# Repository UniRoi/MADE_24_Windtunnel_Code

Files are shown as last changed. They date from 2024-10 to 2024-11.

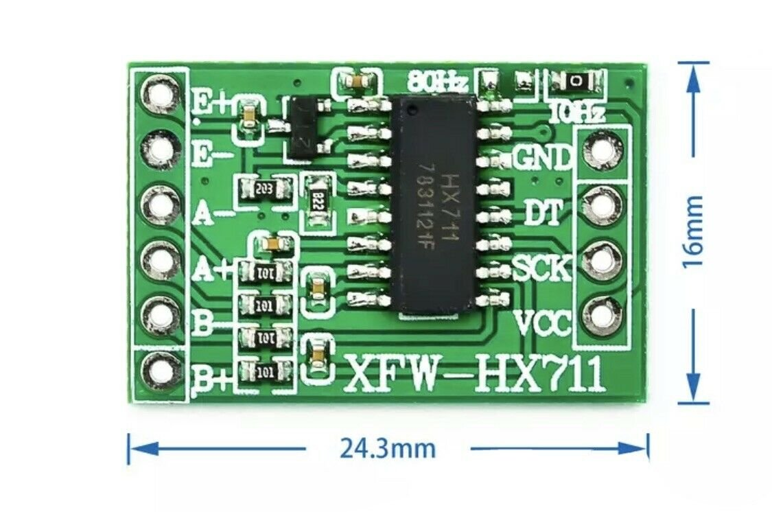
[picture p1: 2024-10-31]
Windtunnel_Schematic/xfw_hx711_picture.png

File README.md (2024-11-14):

# MADE_24_Windtunnel_Code
## Repository for the MADE course at Reykjavik University (RU)
This repository provides resources for the Precision Machine Design course taught in the fall semester of 2024 at Reykjavik University.    
It supports project organization, code structure, and documentation for wind tunnel simulations and data analysis.

## Overview
The MADE_24_Windtunnel_Code repository offers:

### DOCS:
Datasheets, images and project raw data

### Windtunnel_Code:
This folder holds the main code for controlling and operating the wind tunnel system in the `src` and `include` folder.  
Platform IO was used for the development and the library versions are specified in the `platform.ini` file. If this project is compiled for the first time, platform IO will automatically download the necessary libraries and install them on the system.  

The `src_old` folder contains different stages of the project's development:
- `main_calib.cpp`: Initial calibration file from the HX711_ADC library.
- `main_calib_new.cpp`: Modified calibration file from the HX711_ADC library.
- `main_2loadcells.cpp`: First working code for the two-axis load cell
- `main.cpp`: First tests with the LCD.

### Windtunnel_General_Calculations:
Includes general calculation tools, along with pictures and schematics, for analyzing wind tunnel data.  

There are two subfolders in this folder, each requires a virtual pyhton environment to run the jupyter notebook file. Once the environment is created the necessary packages need to be installed with this comand: `pip install -r requirements.txt`
Each folder contains it's own `requirements.txt` file.

#### Evaluating Test Results
Multiple Jupyther notebooks to evaluate the raw data in the `Docs` folder. 

#### Platform Angular Adjustment
Jupyter notebook to calculate the platform angle for different configuration of the linkage.  

### Windtunnel_Schematic:

KICAD 8.0 was used to draw the schematic for the measurement system. This repository also includes a 3D model of the PCB and the libraries for the XFW-HX711 module.

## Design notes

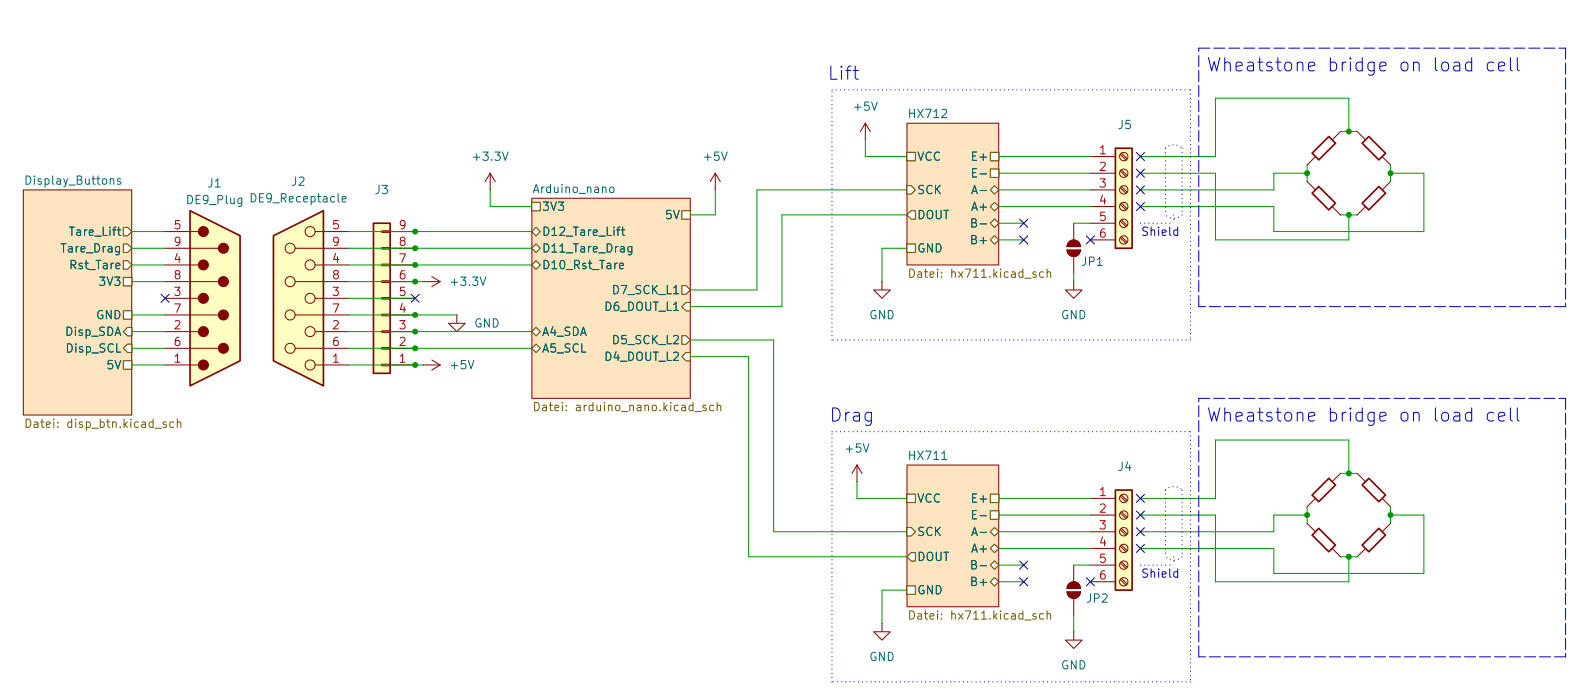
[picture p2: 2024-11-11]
Docs/images/Schematic.png

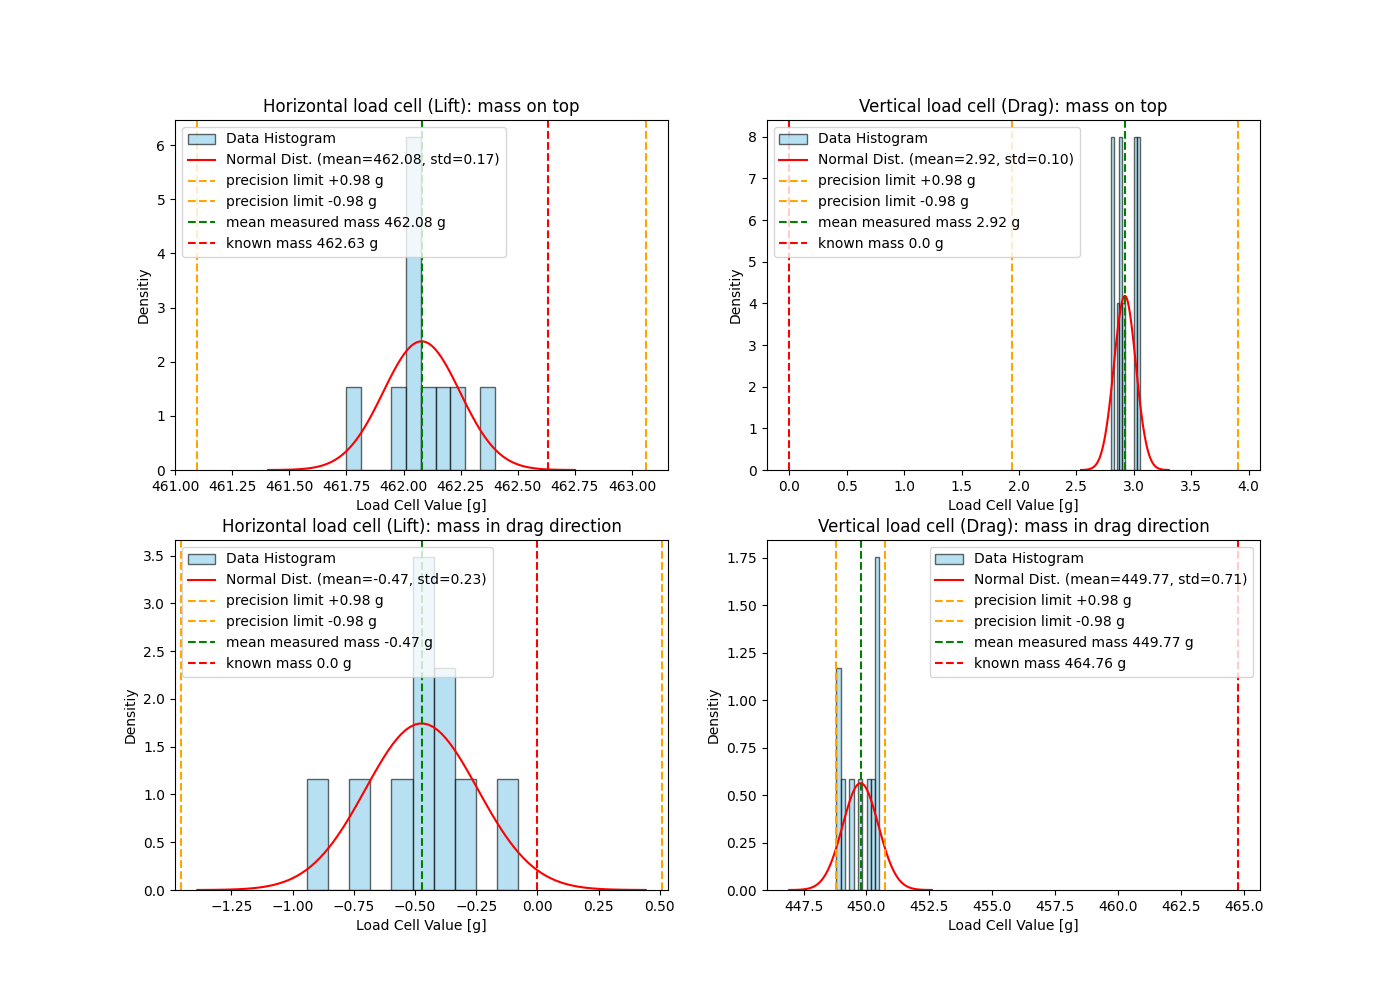
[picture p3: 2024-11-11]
Docs/images/Fullsystem_coupling_lift_drag_precision.png

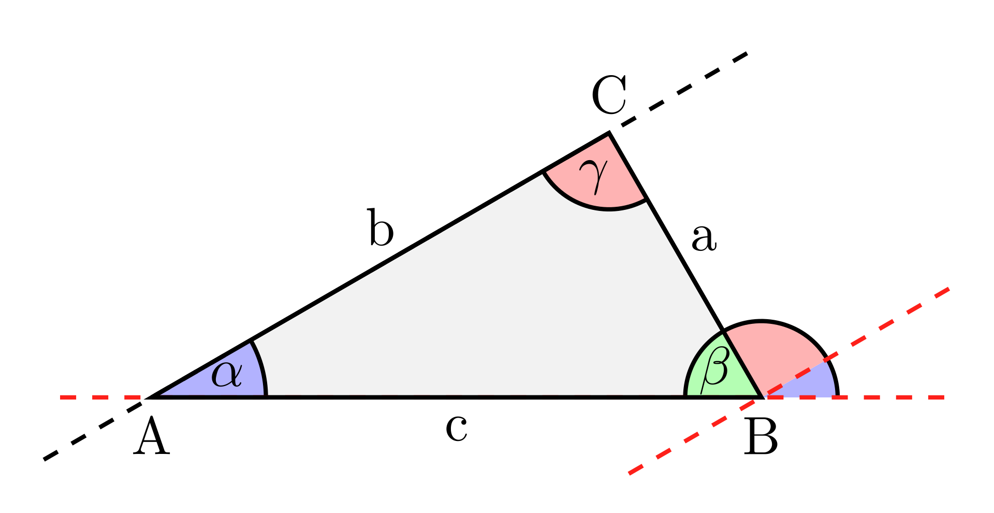
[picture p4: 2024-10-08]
Windtunnel_General_Calculations/Platform_Angular_Adjustment/triangle.png

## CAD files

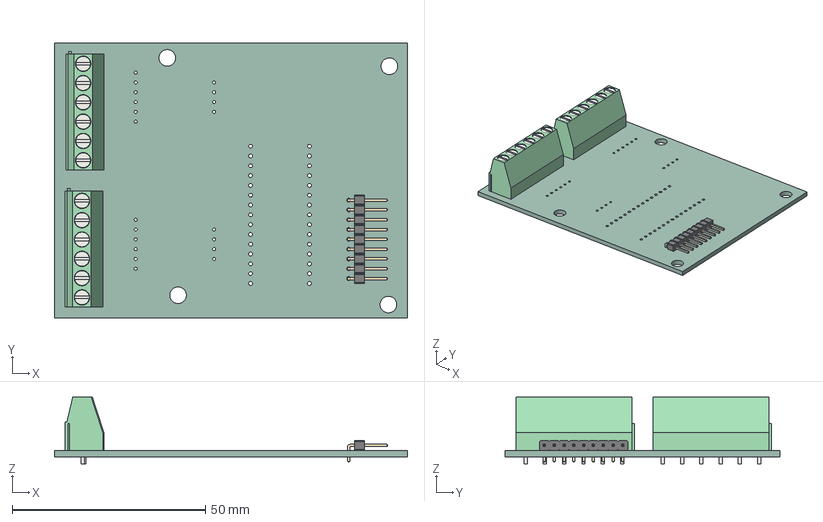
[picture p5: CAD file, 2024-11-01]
Windtunnel_Schematic/Windtunnel_Schematic.step
91.4 x 71.1 x 17.3 mm
TerminalBlock_Phoenix_MKDS_15_6_1x06_P500mm_Horizontal x 2
PinHeader_1x09_P254mm_Horizontal
Windtunnel_Schematic_PCB

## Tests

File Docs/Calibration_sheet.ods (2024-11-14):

Loadcell calibration
 |  |  |  |  | charging |  | charging
 | Load cell 1 3kg |  | Load cell 2 3kg |  | Load cell 3 3kg |  | Load cell 4 5kg |  | Load cell 5 5kg |  | Load cell 6 10kg |  | Load cell 7 10kg |  | Load cell 7.1 10kg
 | light object | heavy object | light object | heavy object | light object | heavy object | light object | heavy object | light object | heavy object | light object | heavy object | light object | heavy object | light object | heavy object
1 | 4,73 | 460,63 | 5,64 | 460,44 | 3,67 | 460,54 | 3,65 | 460,77 | 5,21 | 460,84 | 5,97 | 460,98 | 5,4 | 460,31 | 5,33 | 460,44
2 | 4,83 | 460,59 | 5,6 | 460,54 | 3,52 | 460,66 | 3,82 | 460,92 | 5,32 | 460,72 | 5,65 | 460,97 | 5,25 | 460,51 | 5,52 | 460,5
3 | 4,82 | 460,64 | 5,65 | 460,51 | 3,69 | 460,72 | 3,75 | 460,9 | 5,1 | 460,91 | 6,14 | 460,77 | 5,61 | 460,29 | 5,78 | 460,82
4 | 4,9 | 460,71 | 5,67 | 460,48 | 3,45 | 460,89 | 3,64 | 460,95 | 5,09 | 460,97 | 5,74 | 461,13 | 5,39 | 460,44 | 6,1 | 460,61
5 | 4,87 | 460,62 | 5,66 | 460,54 | 3,2 | 460,95 | 3,71 | 461,02 | 5,26 | 460,89 | 5,91 | 460,82 | 5,48 | 460,58 | 5,26 | 460,67
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

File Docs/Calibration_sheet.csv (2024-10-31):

Loadcell calibration
 |  |  |  |  | charging |  | charging
 | Load cell 1 3kg |  | Load cell 2 3kg |  | Load cell 3 3kg |  | Load cell 4 5kg |  | Load cell 5 5kg |  | Load cell 6 10kg |  | Load cell 7 10kg
 | light object | heavy object | light object | heavy object | light object | heavy object | light object | heavy object | light object | heavy object | light object | heavy object | light object | heavy object
1 | 4,73 | 460,63 | 5,64 | 460,44 | 3,67 | 460,54 | 3,65 | 460,77 | 5,21 | 460,84 | 5,97 | 460,98 | 5,4 | 460,31
2 | 4,83 | 460,59 | 5,6 | 460,54 | 3,52 | 460,66 | 3,82 | 460,92 | 5,32 | 460,72 | 5,65 | 460,97 | 5,25 | 460,51
3 | 4,82 | 460,64 | 5,65 | 460,51 | 3,69 | 460,72 | 3,75 | 460,9 | 5,1 | 460,91 | 6,14 | 460,77 | 5,61 | 460,29
4 | 4,9 | 460,71 | 5,67 | 460,48 | 3,45 | 460,89 | 3,64 | 460,95 | 5,09 | 460,97 | 5,74 | 461,13 | 5,39 | 460,44
5 | 4,87 | 460,62 | 5,66 | 460,54 | 3,2 | 460,95 | 3,71 | 461,02 | 5,26 | 460,89 | 5,91 | 460,82 | 5,48 | 460,58
6 | 4,86 | 460,61 | 5,71 | 460,52 | 3,72 | 460,81 | 3,59 | 460,96 | 5,14 | 461,06 | 6,06 | 461,08 | 5,39 | 460,38
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

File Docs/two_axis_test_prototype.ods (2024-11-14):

statically loaded from the top |  |  |  | statically loaded from the bottom
Load_cell 1 output val | 399,08 | Load_cell 2 output val | -2,57 | Load_cell 1 output val | 399,86 | Load_cell 2 output val | -0,6
Load_cell 1 output val | 399,11 | Load_cell 2 output val | -2,62 | Load_cell 1 output val | 399,93 | Load_cell 2 output val | -0,56
Load_cell 1 output val | 399,17 | Load_cell 2 output val | -2,62 | Load_cell 1 output val | 399,84 | Load_cell 2 output val | -0,52
Load_cell 1 output val | 399,29 | Load_cell 2 output val | -2,67 | Load_cell 1 output val | 399,71 | Load_cell 2 output val | -0,47
Load_cell 1 output val | 399,35 | Load_cell 2 output val | -2,63 | Load_cell 1 output val | 399,85 | Load_cell 2 output val | -0,51
Load_cell 1 output val | 399,5 | Load_cell 2 output val | -2,69 | Load_cell 1 output val | 399,87 | Load_cell 2 output val | -0,59
Load_cell 1 output val | 399,7 | Load_cell 2 output val | -2,77 | Load_cell 1 output val | 399,81 | Load_cell 2 output val | -0,59
Load_cell 1 output val | 399,87 | Load_cell 2 output val | -2,8 | Load_cell 1 output val | 399,96 | Load_cell 2 output val | -0,42
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

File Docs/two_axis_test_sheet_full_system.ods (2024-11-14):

Loading from top |  | Loading in drag direction |  | Loading in drag direction Stiffer setup |  | Loading in drag direction Height adjusted |  | Loading in drag direction Pulley aligned with measurement point
Load cell 7 | Load cell 1 | Load cell 7 | Load cell 1 | Load cell 7 | Load cell 1 | Load cell 7 | Load cell 1 | Load cell 7 | Load cell 1
461,75 | 2,9 | 3,47 | 449,5 | 4,55 | 450,3 | -0,84 | 443,3 | -0,08 | 449
462,05 | 3,05 | 3,69 | 447,88 | 4,5 | 451,22 | -0,97 | 441,84 | -0,94 | 448,81
462 | 2,8 | 3,46 | 448,87 | 4,46 | 451,29 | -0,91 | 441,83 | -0,37 | 448,81
462,07 | 3 | 3,53 | 450,28 | 4,66 | 450,02 | -1,11 | 441,86 | -0,33 | 449,81
462,05 | 2,8 | 3,39 | 447,24 | 4,51 | 448,91 | -1,13 | 443,35 | -0,48 | 450,47
462,08 | 3,02 | 3,35 | 446,79 | 4,38 | 447,17 | -0,96 | 442,34 | -0,36 | 450,52
462,01 | 2,85 | 3,41 | 450,4 | 4,22 | 449,04 | -1,42 | 442,47 | -0,7 | 449,4
462,4 | 2,88 | 3,55 | 448,51 | 4,45 | 451,04 | -1,07 | 441,53 | -0,45 | 450,48
462,24 | 2,89 | 3,71 | 450,19 | 4,38 | 451,16 | -1,19 | 441,78 | -0,5 | 450,05
462,14 | 3,03 | 3,35 | 448,32 | 4,39 | 451,84 | -1,05 | 441,92 | -0,52 | 450,33
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

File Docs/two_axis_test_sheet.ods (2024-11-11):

Two axis test sheet |  | All values are in gramms
 | Loading from bottom |  | Loading from top |  | Loading 90° in drag direction |  |  | Load cell 1 3kg |  | Load cell 7.1 10kg
 | Load cell 7 | Load cell 1 | Load cell 7 | Load cell 1 | Load cell 7 | Load cell 1 |  | light object | heavy object | light object | heavy object
1 | 461,81 | 0,3 | 461,45 | 6,74 | 0,2 | 465,23 | 1 | 4,73 | 460,63 | 5,33 | 460,44
2 | 461,72 | 0,24 | 461,34 | 6,87 | -0,29 | 465,74 | 2 | 4,83 | 460,59 | 5,52 | 460,5
3 | 461,43 | 0,5 | 461,15 | 6,78 | -0,7 | 465,71 | 3 | 4,82 | 460,64 | 5,78 | 460,82
4 | 461,34 | 0,5 | 461,83 | 6,57 | -0,66 | 465,67 | 4 | 4,9 | 460,71 | 6,1 | 460,61
5 | 461,76 | 0,7 | 461,53 | 6,16 | -1,57 | 465,89 | 5 | 4,87 | 460,62 | 5,26 | 460,67
6 | 461,13 | 0,42 | 461,77 | 6,45 | -1,24 | 465,59 | 6 | 4,86 | 460,61 | 5,43 | 460,75
7 | 461,28 | 0,44 | 461,56 | 6,75 | -1,25 | 465,77 | 7 | 4,85 | 460,65 | 5,06 | 460,53
8 | 461,26 | 0,78 | 461,3 | 6,68 | -1,53 | 465,65
9 | 461,17 | 0,81 | 461,39 | 6,35 | -0,5 | 465,66 |  | Calibration value | 1480.38 | Calibration value | 429.83
10 | 461,15 | 0,55 | 461,58 | 6,76 | -1,45 | 465,8 |  | Offset value | 8476668 | Offset value | 8370961
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

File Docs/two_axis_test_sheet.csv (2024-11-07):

Loading from bottom |  | Loading from top |  | Loading 90° in drag direction
Load cell 7 | Load cell 3 | Load cell 7 | Load cell 3 | Load cell 7 | Load cell 3
461,81 | 0,3 | 461,45 | 6,74 | 0,2 | 465,23
461,72 | 0,24 | 461,34 | 6,87 | -0,29 | 465,74
461,43 | 0,5 | 461,15 | 6,78 | -0,7 | 465,71
461,34 | 0,5 | 461,83 | 6,57 | -0,66 | 465,67
461,76 | 0,7 | 461,53 | 6,16 | -1,57 | 465,89
461,13 | 0,42 | 461,77 | 6,45 | -1,24 | 465,59
461,28 | 0,44 | 461,56 | 6,75 | -1,25 | 465,77
461,26 | 0,78 | 461,3 | 6,68 | -1,53 | 465,65
461,17 | 0,81 | 461,39 | 6,35 | -0,5 | 465,66
461,15 | 0,55 | 461,58 | 6,76 | -1,45 | 465,8
mean drag | 0,524 | mean drag | 6,611 | mean drag | 465,671
mean lift | 461,405 | mean lift | 461,49 | mean lift | -0,899
std drag | 0,191148575139282 | std drag | 0,225509300128497 | std drag | 0,177103234175871
std lift | 0,26387075961118 | std lift | 0,209337579574767 | std lift | 0,598710651687812
Known mass | 462,6

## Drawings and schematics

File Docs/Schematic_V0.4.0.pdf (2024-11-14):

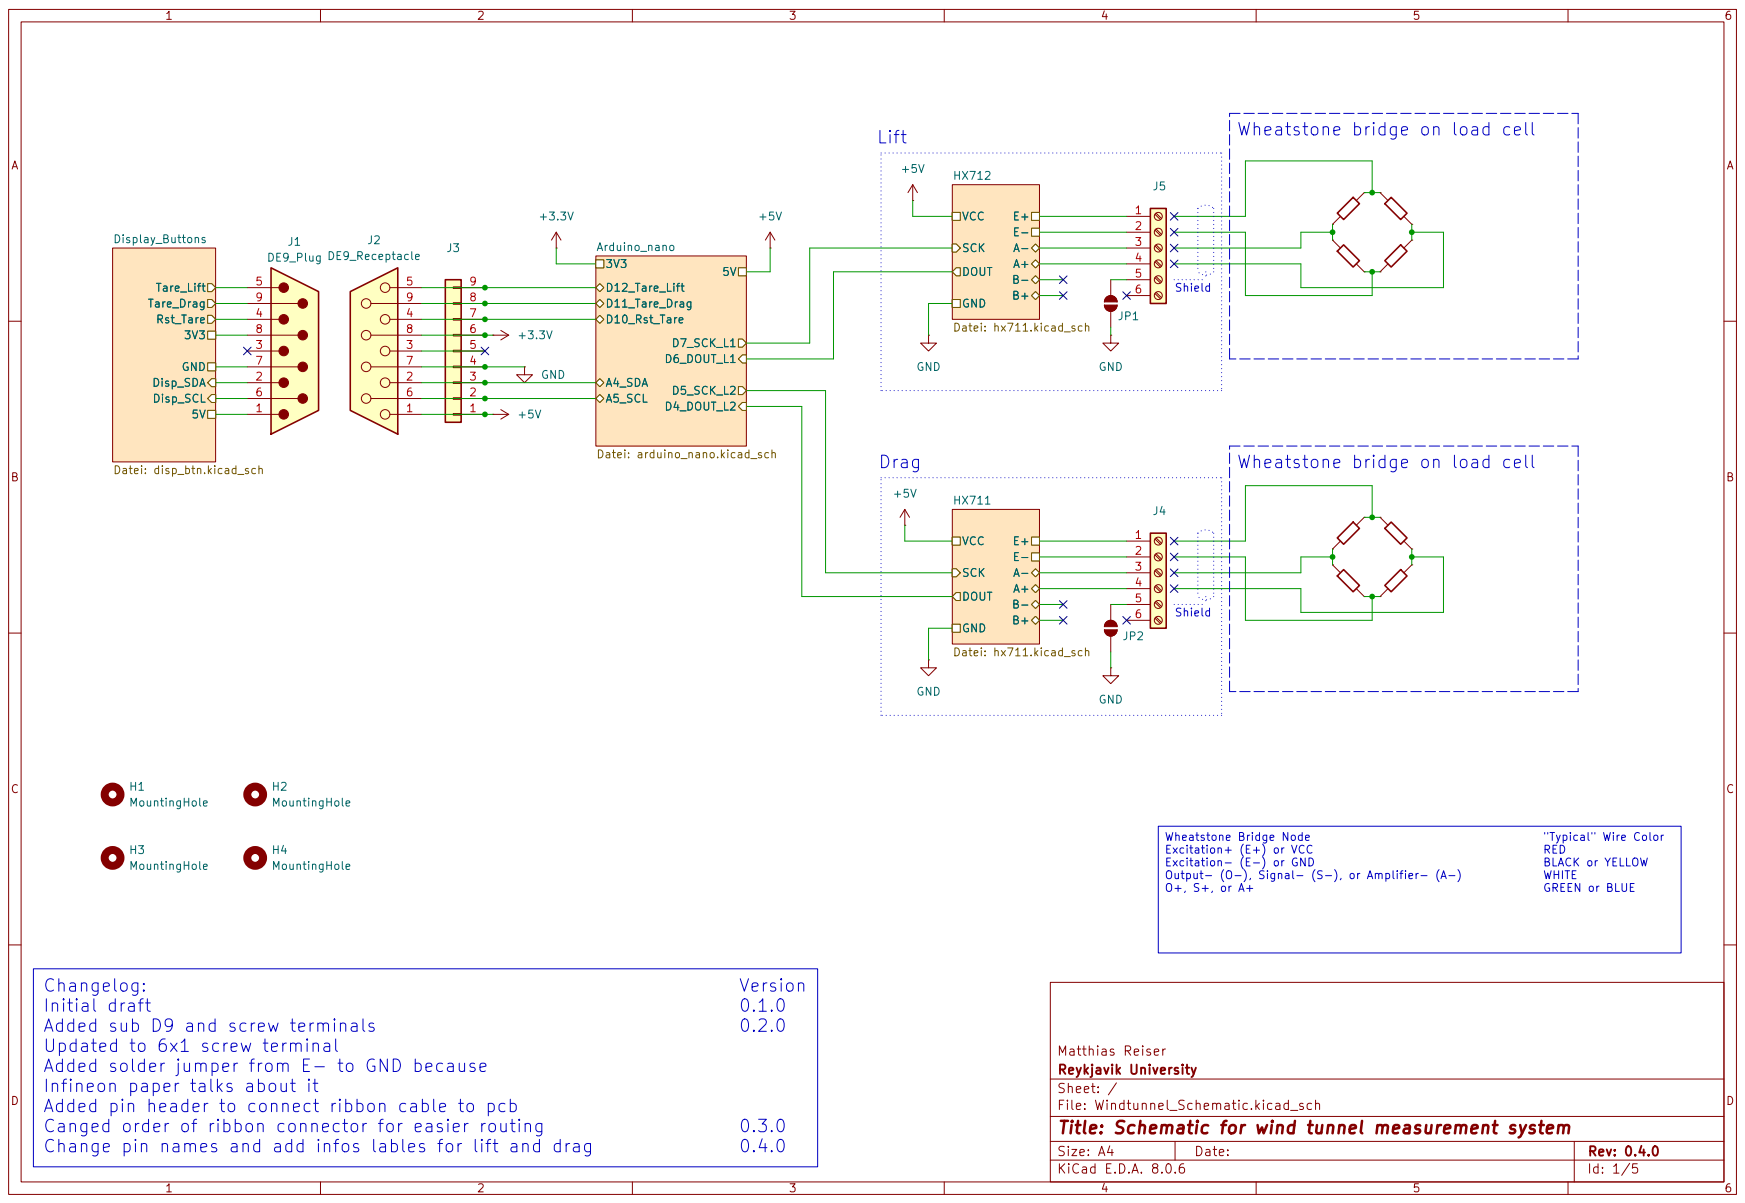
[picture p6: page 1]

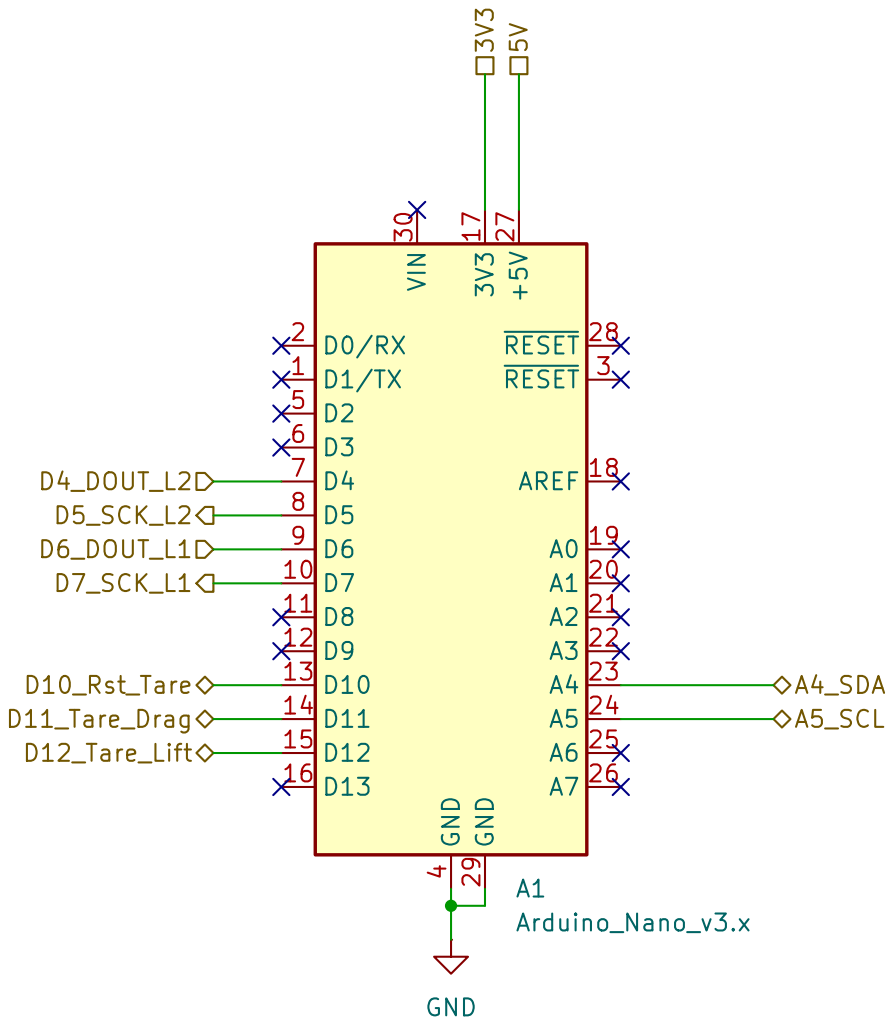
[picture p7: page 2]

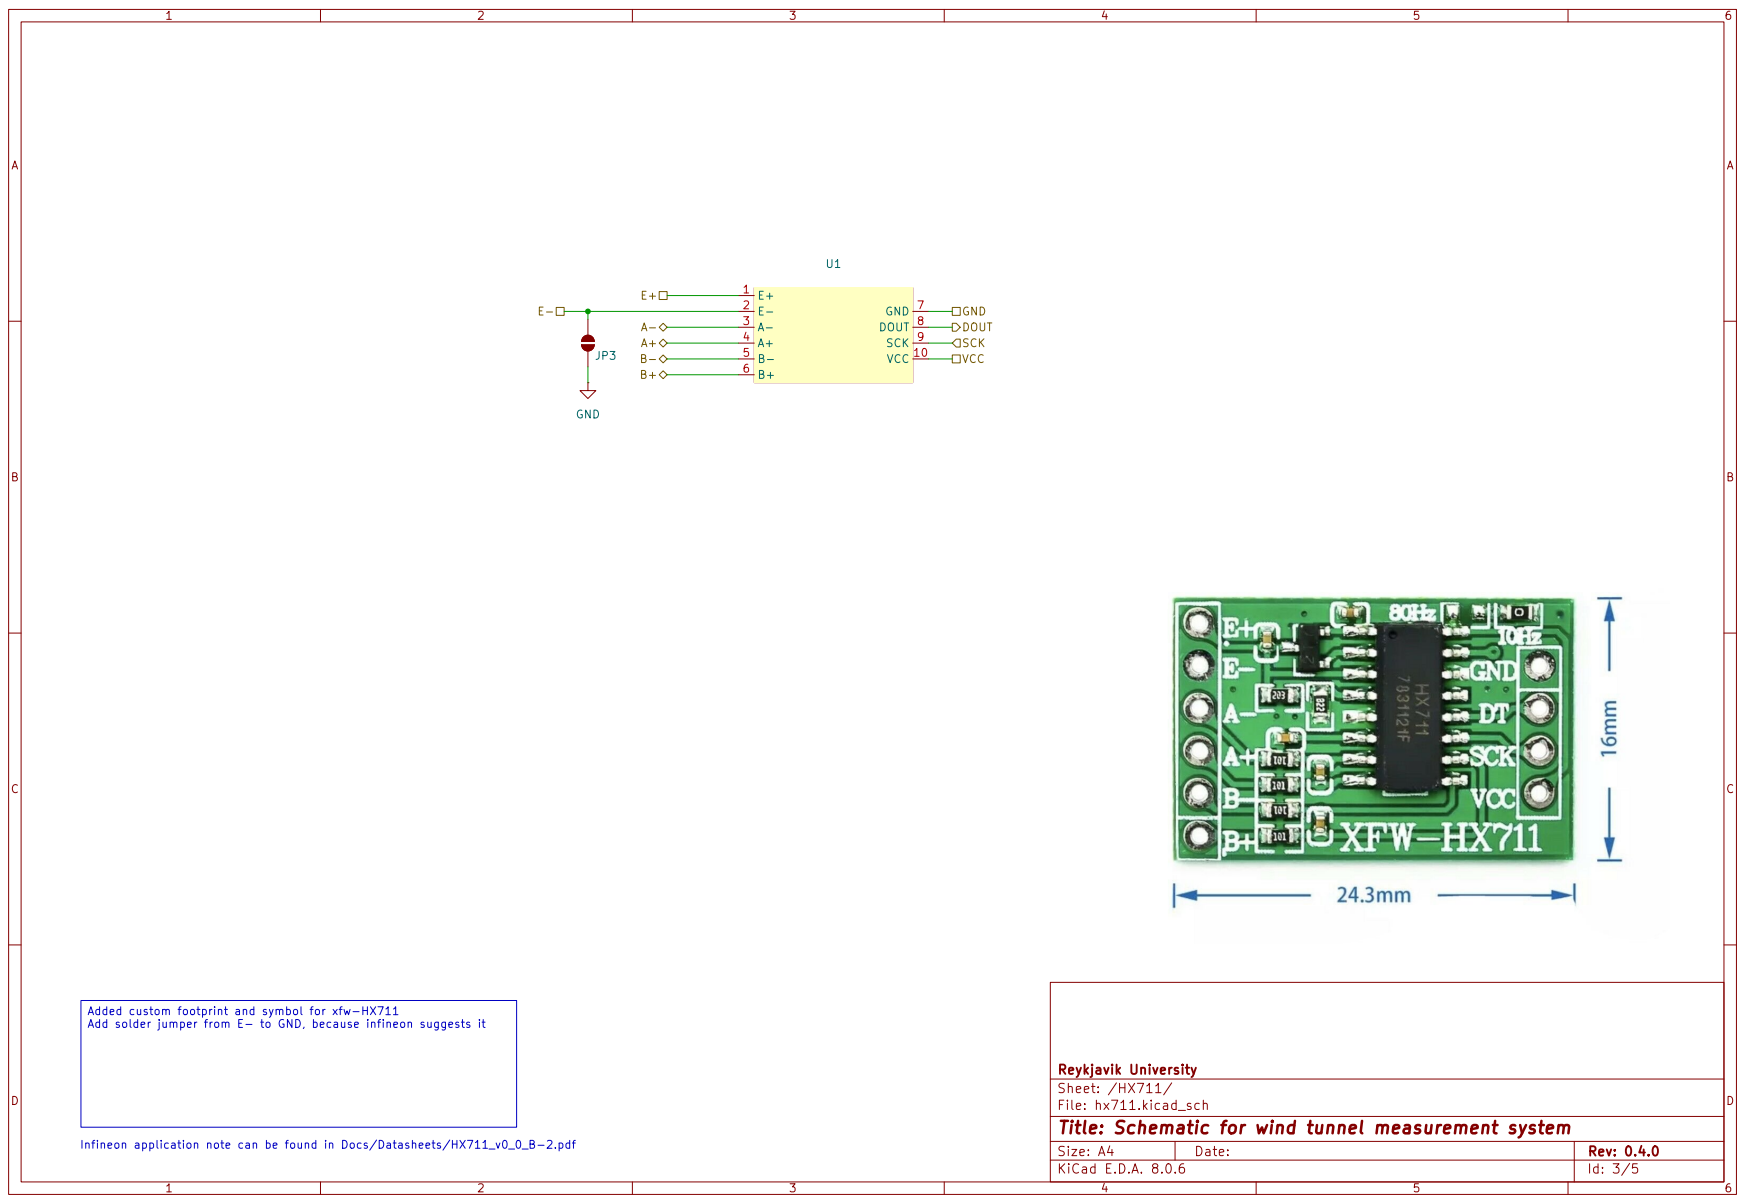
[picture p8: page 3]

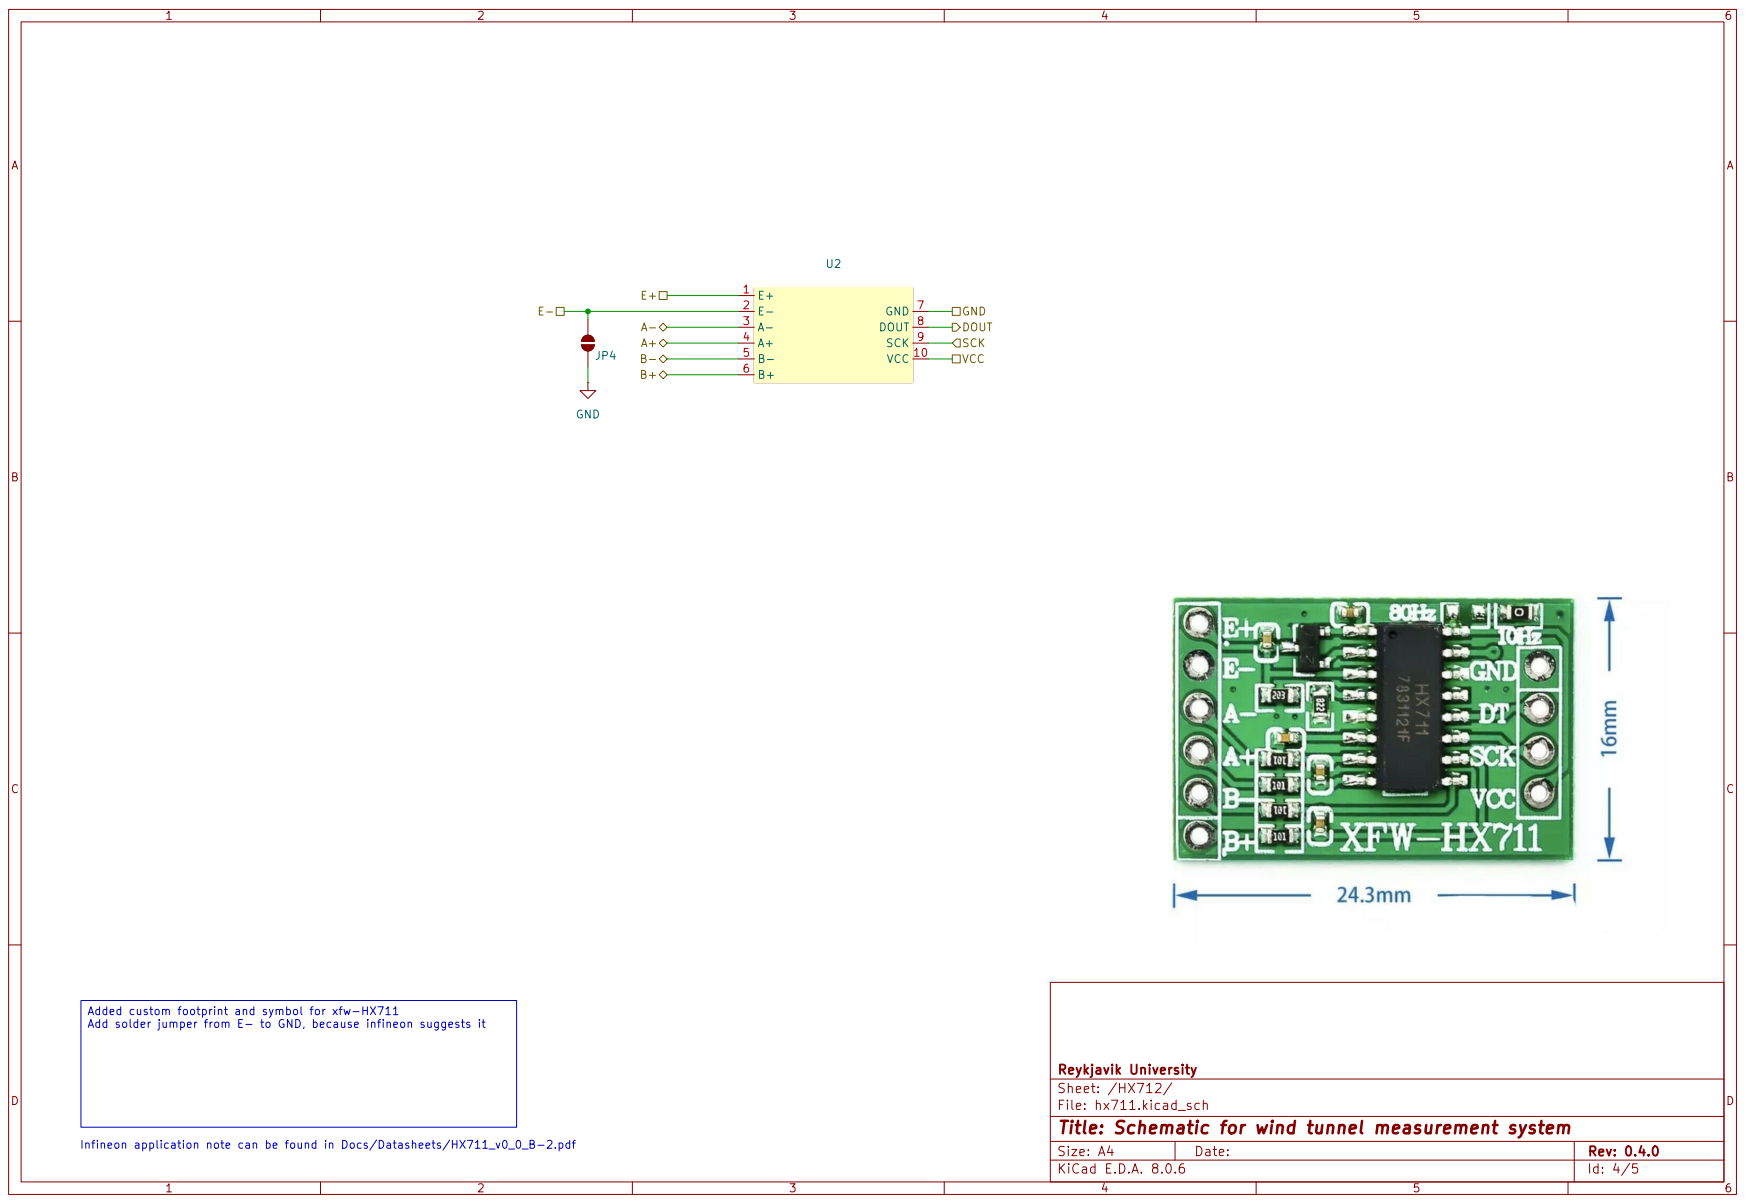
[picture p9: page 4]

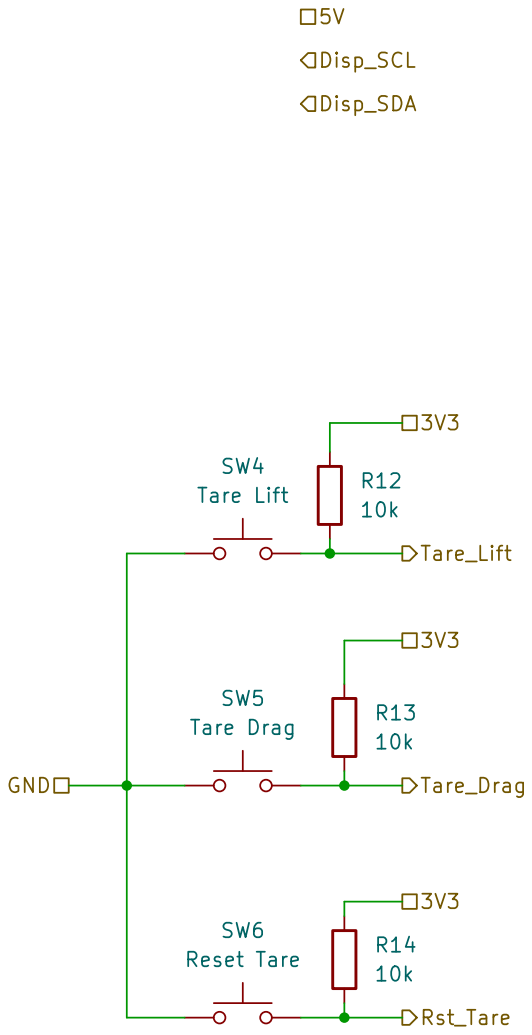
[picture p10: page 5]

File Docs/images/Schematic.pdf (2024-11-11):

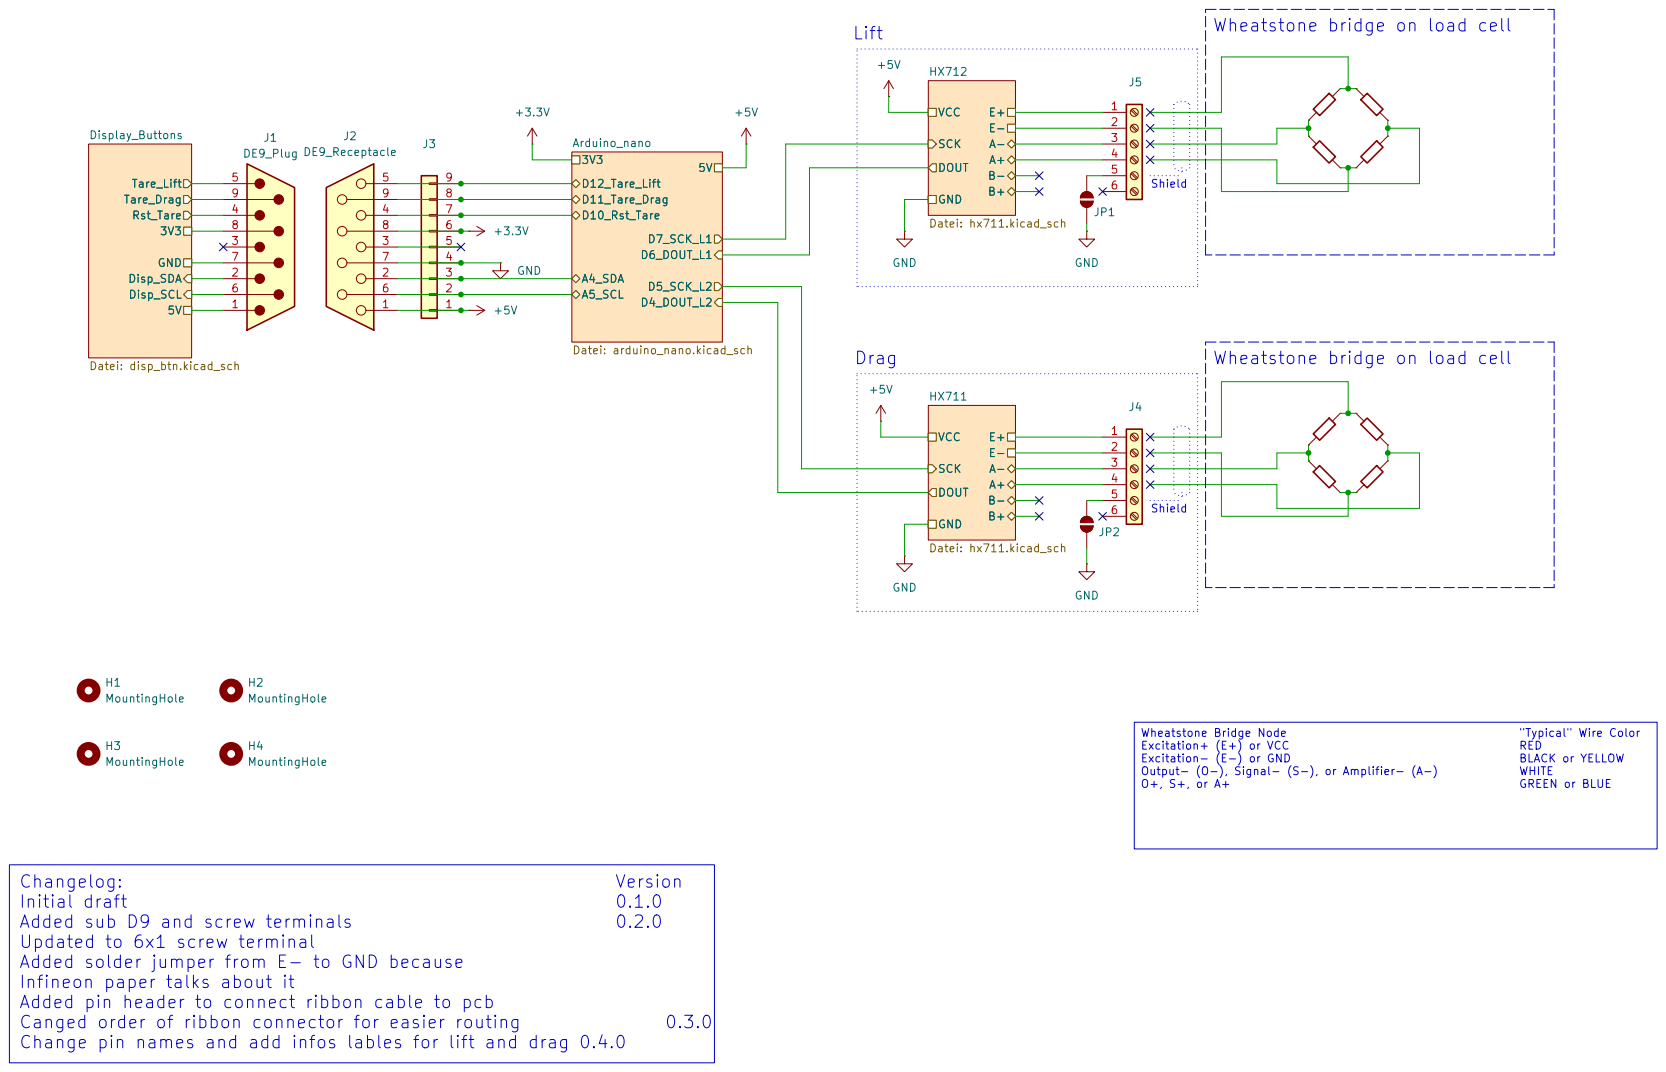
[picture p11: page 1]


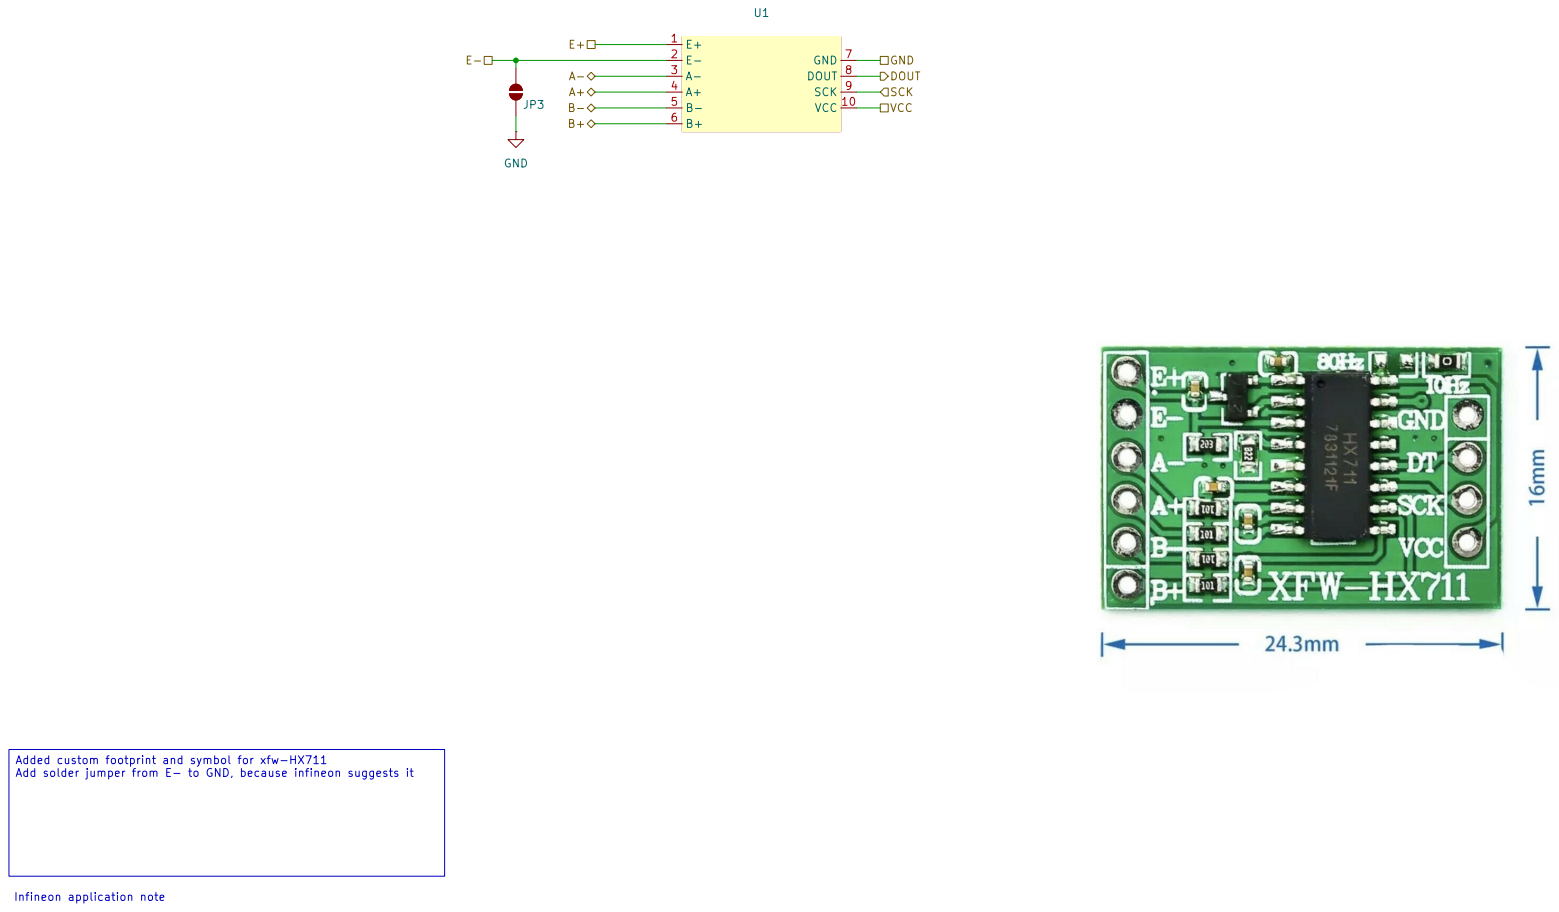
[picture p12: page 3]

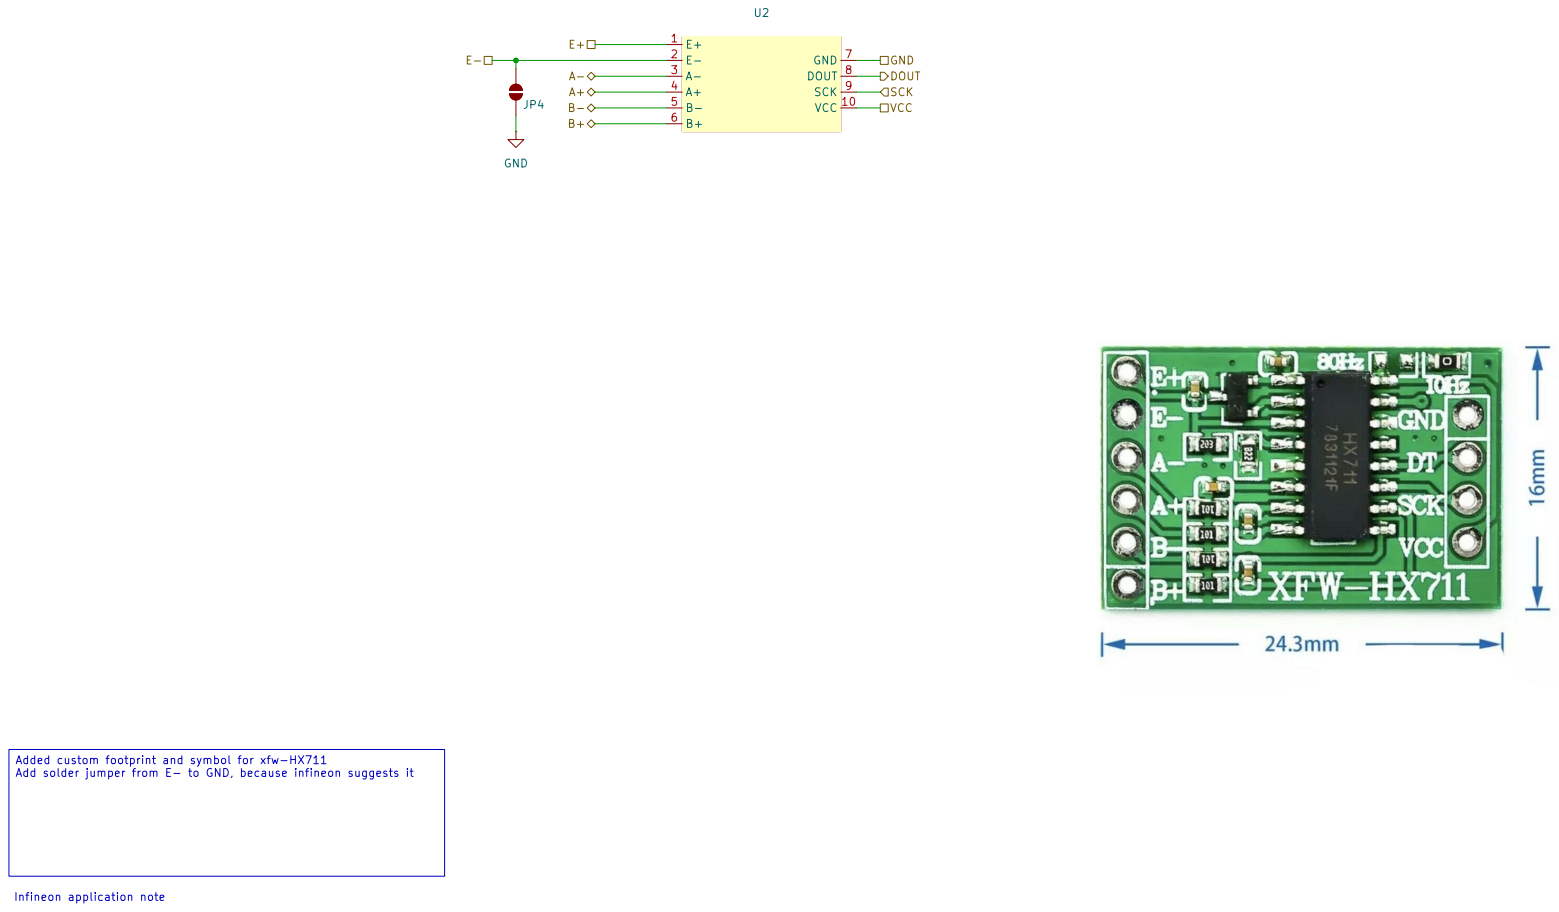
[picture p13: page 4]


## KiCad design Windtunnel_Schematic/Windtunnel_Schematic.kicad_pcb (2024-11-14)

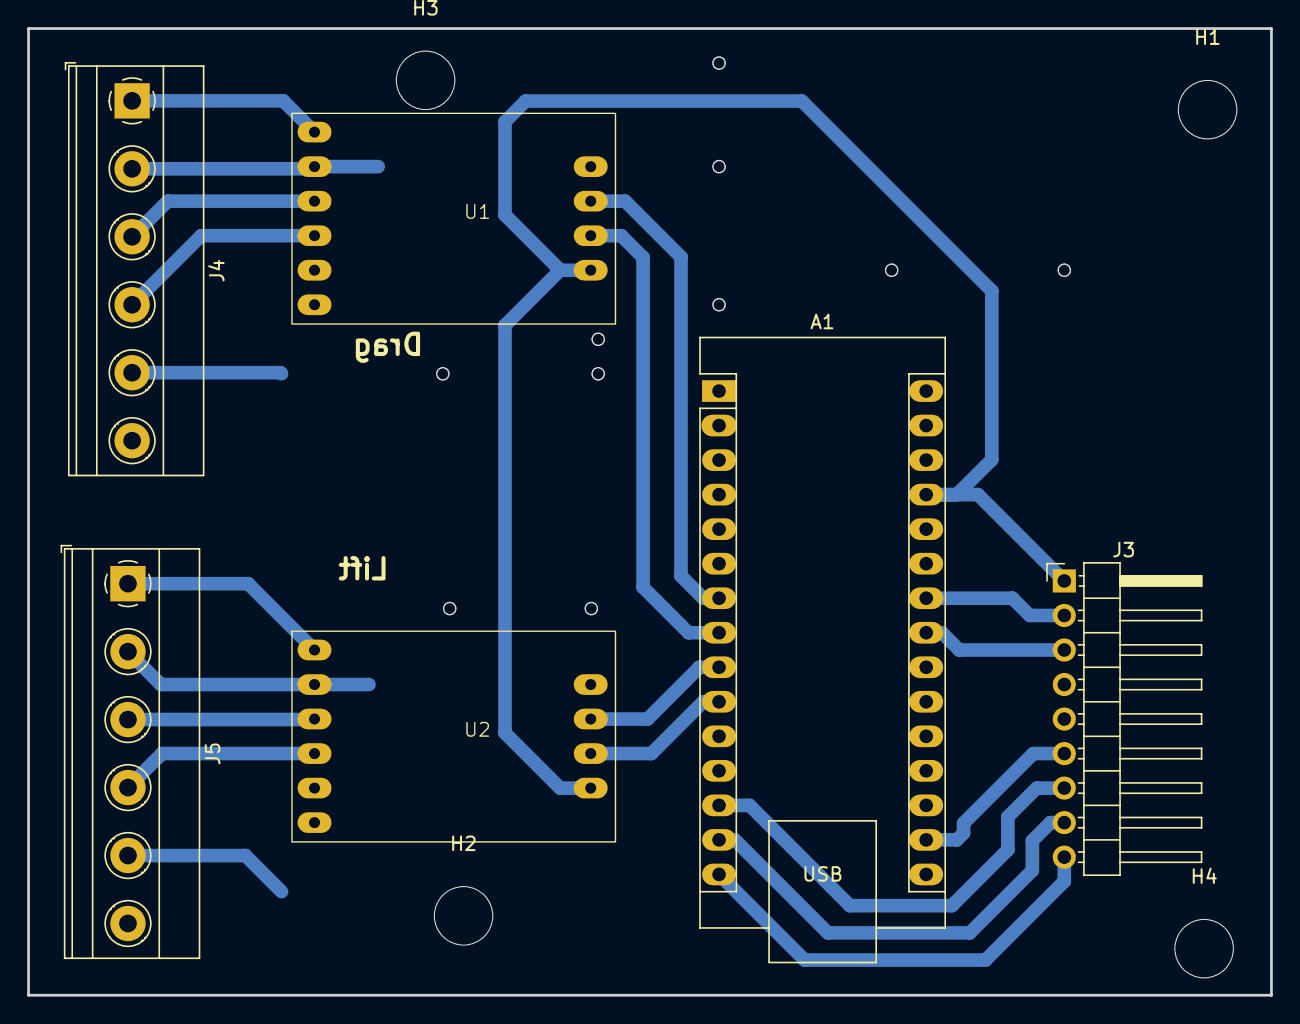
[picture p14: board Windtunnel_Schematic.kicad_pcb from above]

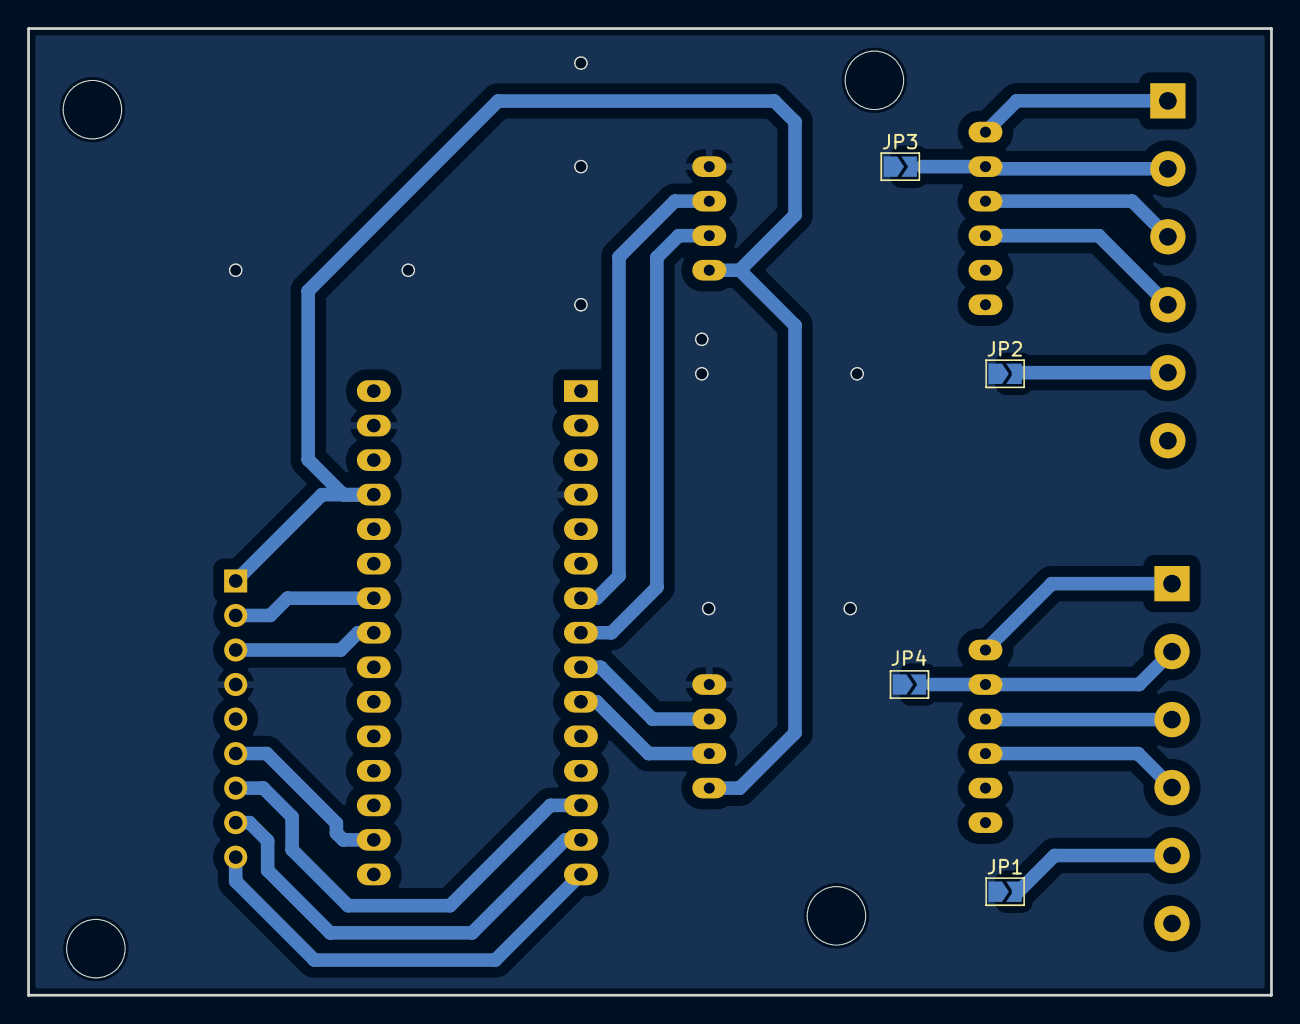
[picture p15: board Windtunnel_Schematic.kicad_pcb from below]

Board: 2 copper layers, 91.4 x 71.1 mm, 14 parts (4 on the bottom side), 22 nets.

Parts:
A1: Arduino_Nano_v3.x; Arduino_Nano
H1, H2, H3, H4: MountingHole; MountingHole_4.3mm_M4
J3: Conn_01x09; PinHeader_1x09_P2.54mm_Horizontal
J4, J5: Screw_Terminal_01x06; TerminalBlock_Phoenix_MKDS-1,5-6_1x06_P5.00mm_Horizontal
JP1, JP2, JP3, JP4: SolderJumper_2_Open; SolderJumper-2_P1.3mm_Open_TrianglePad1.0x1.5mm
U1, U2: xfw_hx711

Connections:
+3.3V: A1.17 (3V3), J3.6
+5V: A1.27 (+5V), J3.1, U1.10 (VCC), U2.10 (VCC)
/Arduino_nano/A4_SDA: A1.23 (A4), J3.3
/Arduino_nano/A5_SCL: A1.24 (A5), J3.2
/Arduino_nano/D4_DOUT_L2: A1.7 (D4), U1.8 (DOUT)
/Arduino_nano/D5_SCK_L2: A1.8 (D5), U1.9 (SCK)
/Arduino_nano/D6_DOUT_L1: A1.9 (D6), U2.8 (DOUT)
/Arduino_nano/D7_SCK_L1: A1.10 (D7), U2.9 (SCK)
/Arduino_nano/D11: A1.13 (D10), J3.7
/Arduino_nano/D12: A1.14 (D11), J3.8
/Arduino_nano/D13: A1.15 (D12), J3.9
/HX711/A+: J4.4, U1.4 (A+)
/HX711/A-: J4.3, U1.3 (A-)
/HX711/E+: J4.1, U1.1 (E+)
/HX711/E-: J4.2, JP3.2 (B), U1.2 (E-)
/HX712/A+: J5.4, U2.4 (A+)
/HX712/A-: J5.3, U2.3 (A-)
/HX712/E+: J5.1, U2.1 (E+)
/HX712/E-: J5.2, JP4.2 (B), U2.2 (E-)
GND: A1.4 (GND), A1.29 (GND), J3.4, JP1.1 (A), JP2.1 (A), JP3.1 (A), JP4.1 (A), U1.7 (GND), U2.7 (GND)
unnamed: J4.5, JP2.2 (B)
unnamed: J5.5, JP1.2 (B)

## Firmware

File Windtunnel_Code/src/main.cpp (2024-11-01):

/* Measurement system for low speed wind tunnel */
//-------------------------------------------------------------------------------------
// This code calculates lift and drag forces on the new 2-axis force measurement system
// at the University of Reykjavik
// It uses the Arduino master library for HX711 24-Bit Analog-to-Digital Converter for Weigh Scales
// from Olav Kallhovd
// Code was developed during the masters class Precision Machine Design in the FALL semester 2024
// Code was written by Matthias Reiser

//-------------------------------------------------------------------------------------
// HX711_ADC.h
// Arduino master library for HX711 24-Bit Analog-to-Digital Converter for Weigh Scales
// Olav Kallhovd sept2017
// Tested with      : HX711 asian module on channel A and YZC-133 3kg load cell
// Tested with MCU  : Arduino Nano
//-------------------------------------------------------------------------------------
// This is an example sketch on how to use this library for two ore more HX711 modules
// Settling time (number of samples) and data filtering can be adjusted in the config.h file

/* Measurement system for low speed wind tunnel */
/* two HX711 amplifiers are used for a 2 axis load cell
   three buttons are used
   two of those tare lift and drag force
   one is to reset the tare values for this the tare offset for 0g needs to be saved in eeprom or written into the scetch, when calibrating the loadcell
   a 2x16 lcd display is used for displaying the measured forces */

#include <HX711_ADC.h>
#if defined(ESP8266) || defined(ESP32) || defined(AVR)
#include <EEPROM.h>
#endif

#include <Wire.h>
#include "button.h"
#include "Calc_Newton.h"
#include "version.h"
#include "stdbool.h"
#include "LCDDisplay.h"
#include <LiquidCrystal_I2C.h>
#include "Calc_Newton.h"

LCDDisplay lcd(0x27, 16, 2); // set the LCD address to 0x27 for a 16 chars and 2 line display
// LiquidCrystal_I2C lcd_raw(0x27, 16, 2);

// pins:
const int HX711_dout_2 = 4; // mcu > HX711 no 2 dout pin
const int HX711_sck_2 = 5;  // mcu > HX711 no 2 sck pin
const int HX711_dout_1 = 6; // mcu > HX711 no 1 dout pin
const int HX711_sck_1 = 7;  // mcu > HX711 no 1 sck pin

// HX711 constructor (dout pin, sck pin)
HX711_ADC LoadCell_lift(HX711_dout_1, HX711_sck_1); // HX711 1
HX711_ADC LoadCell_drag(HX711_dout_2, HX711_sck_2); // HX711 2

const int calVal_eepromAdress_1 = 0; // eeprom adress for calibration value load cell 1 (4 bytes)
const int calVal_eepromAdress_2 = 4; // eeprom adress for calibration value load cell 2 (4 bytes)
const int tareVal_eepromAdress_1 = 8;  // eeprom adress for tare value load cell 1 (8 bytes)
const int tareVal_eepromAdress_2 = 16; // eeprom adress for tare value load cell 2 (8 bytes)
unsigned long t = 0;

button BtnTareLift;
button BtnTareDrag;
button BtnRstTare;

version Version;

static char m_acRow[16] = "Ver: ";

static long tareValue_lift; // tare value load cell 1 for zero weight
static long tareValue_drag; // tare value load cell 2 for zero weight

void setup()
{
  BtnTareLift.init(12);
  BtnTareDrag.init(11);
  BtnRstTare.init(10);
  lcd.init();

  Serial.begin(57600);
  delay(10);
  Serial.println();
  Serial.println("Starting...");

  Version.getString(&m_acRow[5]);
  lcd.writeFixedRows(m_acRow, "Status: Ready"); // Write to both rows


  float calibrationValue_lift; // calibration value load cell 1
  float calibrationValue_drag; // calibration value load cell 2



  calibrationValue_lift = 429.83; // uncomment this if you want to set this value in the sketch
  calibrationValue_drag = 1480.38; // uncomment this if you want to set this value in the sketch
  tareValue_lift = 8370961;
  tareValue_drag = 8476668;
#if defined(ESP8266) || defined(ESP32)
  // EEPROM.begin(512); // uncomment this if you use ESP8266 and want to fetch the value from eeprom
#endif
  // EEPROM.get(calVal_eepromAdress_1, calibrationValue_lift); // uncomment this if you want to fetch the value from eeprom
  // EEPROM.get(calVal_eepromAdress_2, calibrationValue_drag); // uncomment this if you want to fetch the value from eeprom
  // EEPROM.get(tareVal_eepromAdress_1, tareValue_lift); // uncomment this if you want to fetch the value from eeprom
  // EEPROM.get(tareVal_eepromAdress_2, tareValue_drag); // uncomment this if you want to fetch the value from eeprom

  LoadCell_lift.begin();
  LoadCell_drag.begin();
  // LoadCell_lift.setReverseOutput();
  // LoadCell_drag.setReverseOutput();
  unsigned long stabilizingtime = 2000; // tare preciscion can be improved by adding a few seconds of stabilizing time
  bool _tare = false;                    // set this to false if you don't want tare to be performed in the next step
  uint8_t loadcell_1_rdy = 0;
  uint8_t loadcell_2_rdy = 0;

  while ((loadcell_1_rdy + loadcell_2_rdy) < 2)
  { // run startup, stabilization and tare, both modules simultaniously
    if (!loadcell_1_rdy)
    {
      loadcell_1_rdy = LoadCell_lift.startMultiple(stabilizingtime, _tare);
    }
    if (!loadcell_2_rdy)
    {
      loadcell_2_rdy = LoadCell_drag.startMultiple(stabilizingtime, _tare);
    }
  }

  if (LoadCell_lift.getTareTimeoutFlag())
  {
    Serial.println("Timeout, check MCU>HX711 lift wiring and pin designations");
  }
  if (LoadCell_drag.getTareTimeoutFlag())
  {
    Serial.println("Timeout, check MCU>HX711 drag wiring and pin designations");
  }

  LoadCell_lift.setCalFactor(calibrationValue_lift); // user set calibration value (float)
  LoadCell_drag.setCalFactor(calibrationValue_drag); // user set calibration value (float)
  Serial.println("Startup is complete");
}

/* Measurement system for low speed wind tunnel */
static char m_acLift[16] = {0};
static char m_acDrag[16] = {0};
void loop()
{
  static bool newDataReady = false;
  const int serialPrintInterval = 100; // increase value to slow down serial print activity

  // check for new data/start next conversion:
  if (LoadCell_lift.update())
  {
    newDataReady = true;
  }
  LoadCell_drag.update();

  // get smoothed value from data set
  if ((newDataReady))
  {
    if (millis() > t + serialPrintInterval)
    {
      char tempStr[8];
      float a = LoadCell_lift.getData();
      float b = LoadCell_drag.getData();
      long offset = LoadCell_drag.getTareOffset();

      float liftN = convertToNewtons(a);
      float DragN = convertToNewtons(b);
      dtostrf(liftN, 6, 2, tempStr);
      snprintf(m_acLift, sizeof(m_acLift), "Lift: %sN", tempStr);
      dtostrf(DragN, 6, 3, tempStr);
      snprintf(m_acDrag, sizeof(m_acDrag), "Drag: %sN", tempStr);
      Serial.print("Load_cell 1 output val: ");
      Serial.print(a);
      Serial.print("    Drag tare offest: ");
      Serial.print(offset);
      Serial.print("    Load_cell 2 output val: ");
      Serial.println(b);
      newDataReady = false;
      t = millis();

      lcd.writeFixedRows(m_acLift, m_acDrag);
    }
  }

  // receive command from serial terminal, send 't' to initiate tare operation:
  if (Serial.available() > 0)
  {
    char inByte = Serial.read();
    if (inByte == 't')
    {
      LoadCell_lift.tareNoDelay();
      LoadCell_drag.tareNoDelay();
    }
    if(inByte == 'r')
    {
     long offset = LoadCell_lift.getTareOffset(); 
     
     float callift = LoadCell_lift.getCalFactor();
    LoadCell_lift.setTareOffset(offset/callift);
    }
  }

  if(BtnTareLift.was_pressed() == true)
  {
    LoadCell_lift.tareNoDelay();
  }

  if(BtnTareDrag.was_pressed() == true)
  {
    LoadCell_drag.tareNoDelay();
  }

  if(BtnRstTare.was_pressed() == true)
  {
    LoadCell_lift.setTareOffset(tareValue_lift);
    LoadCell_drag.setTareOffset(tareValue_drag);
  }



  // check if last tare operation is complete
  if (LoadCell_lift.getTareStatus() == true)
  {
    Serial.println("Tare load cell 1 complete");
  }
  if (LoadCell_drag.getTareStatus() == true)
  {
    Serial.println("Tare load cell 2 complete");
  }
}

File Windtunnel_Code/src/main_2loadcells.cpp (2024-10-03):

//-------------------------------------------------------------------------------------
// HX711_ADC.h
// Arduino master library for HX711 24-Bit Analog-to-Digital Converter for Weigh Scales
// Olav Kallhovd sept2017
// Tested with      : HX711 asian module on channel A and YZC-133 3kg load cell
// Tested with MCU  : Arduino Nano
//-------------------------------------------------------------------------------------
// This is an example sketch on how to use this library for two ore more HX711 modules
// Settling time (number of samples) and data filtering can be adjusted in the config.h file

#include <HX711_ADC.h>
#if defined(ESP8266)|| defined(ESP32) || defined(AVR)
#include <EEPROM.h>
#endif

#include <Wire.h>

//pins:
const int HX711_dout_1 = 4; //mcu > HX711 no 1 dout pin
const int HX711_sck_1 = 5; //mcu > HX711 no 1 sck pin
const int HX711_dout_2 = 6; //mcu > HX711 no 2 dout pin
const int HX711_sck_2 = 7; //mcu > HX711 no 2 sck pin

//HX711 constructor (dout pin, sck pin)
HX711_ADC LoadCell_1(HX711_dout_1, HX711_sck_1); //HX711 1
HX711_ADC LoadCell_2(HX711_dout_2, HX711_sck_2); //HX711 2

const int calVal_eepromAdress_1 = 0; // eeprom adress for calibration value load cell 1 (4 bytes)
const int calVal_eepromAdress_2 = 4; // eeprom adress for calibration value load cell 2 (4 bytes)
unsigned long t = 0;

void setup() {
  Serial.begin(57600); delay(10);
  Serial.println();
  Serial.println("Starting...");

  float calibrationValue_1; // calibration value load cell 1
  float calibrationValue_2; // calibration value load cell 2

  calibrationValue_1 = 696.0; // uncomment this if you want to set this value in the sketch
  calibrationValue_2 = 733.0; // uncomment this if you want to set this value in the sketch
#if defined(ESP8266) || defined(ESP32)
  //EEPROM.begin(512); // uncomment this if you use ESP8266 and want to fetch the value from eeprom
#endif
  EEPROM.get(calVal_eepromAdress_1, calibrationValue_1); // uncomment this if you want to fetch the value from eeprom
  EEPROM.get(calVal_eepromAdress_2, calibrationValue_2); // uncomment this if you want to fetch the value from eeprom

  LoadCell_1.begin();
  LoadCell_2.begin();
  //LoadCell_1.setReverseOutput();
  //LoadCell_2.setReverseOutput();
  unsigned long stabilizingtime = 2000; // tare preciscion can be improved by adding a few seconds of stabilizing time
  boolean _tare = true; //set this to false if you don't want tare to be performed in the next step
  byte loadcell_1_rdy = 0;
  byte loadcell_2_rdy = 0;
  while ((loadcell_1_rdy + loadcell_2_rdy) < 2) { //run startup, stabilization and tare, both modules simultaniously
    if (!loadcell_1_rdy) loadcell_1_rdy = LoadCell_1.startMultiple(stabilizingtime, _tare);
    if (!loadcell_2_rdy) loadcell_2_rdy = LoadCell_2.startMultiple(stabilizingtime, _tare);
  }
  if (LoadCell_1.getTareTimeoutFlag()) {
    Serial.println("Timeout, check MCU>HX711 no.1 wiring and pin designations");
  }
  if (LoadCell_2.getTareTimeoutFlag()) {
    Serial.println("Timeout, check MCU>HX711 no.2 wiring and pin designations");
  }
  LoadCell_1.setCalFactor(calibrationValue_1); // user set calibration value (float)
  LoadCell_2.setCalFactor(calibrationValue_2); // user set calibration value (float)
  Serial.println("Startup is complete");
}

void loop() {
  static boolean newDataReady = 0;
  const int serialPrintInterval = 0; //increase value to slow down serial print activity

  // check for new data/start next conversion:
  if (LoadCell_1.update()) newDataReady = true;
  LoadCell_2.update();

  //get smoothed value from data set
  if ((newDataReady)) {
    if (millis() > t + serialPrintInterval) {
      float a = LoadCell_1.getData();
      float b = LoadCell_2.getData();
      Serial.print("Load_cell 1 output val: ");
      Serial.print(a);
      Serial.print("    Load_cell 2 output val: ");
      Serial.println(b);
      newDataReady = 0;
      t = millis();
    }
  }

  // receive command from serial terminal, send 't' to initiate tare operation:
  if (Serial.available() > 0) {
    char inByte = Serial.read();
    if (inByte == 't') {
      LoadCell_1.tareNoDelay();
      LoadCell_2.tareNoDelay();
    }
  }

  //check if last tare operation is complete
  if (LoadCell_1.getTareStatus() == true) {
    Serial.println("Tare load cell 1 complete");
  }
  if (LoadCell_2.getTareStatus() == true) {
    Serial.println("Tare load cell 2 complete");
  }
}

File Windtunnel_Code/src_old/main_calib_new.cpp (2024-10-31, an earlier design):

/*
   -------------------------------------------------------------------------------------
   HX711_ADC
   Arduino library for HX711 24-Bit Analog-to-Digital Converter for Weight Scales
   Olav Kallhovd sept2017
   -------------------------------------------------------------------------------------
*/

/*
   This example file shows how to calibrate the load cell and optionally store the calibration
   value in EEPROM, and also how to change the value manually.
   The result value can then later be included in your project sketch or fetched from EEPROM.

   To implement calibration in your project sketch the simplified procedure is as follow:
       LoadCell.tare();
       //place known mass
       LoadCell.refreshDataSet();
       float newCalibrationValue = LoadCell.getNewCalibration(known_mass);
*/

#include <HX711_ADC.h>
#if defined(ESP8266)|| defined(ESP32) || defined(AVR)
#include <EEPROM.h>
#endif

#include <Wire.h>

static int Num_LoadCell = 0;

//pins:
const int HX711_dout = 4; //mcu > HX711 dout pin
const int HX711_sck = 5; //mcu > HX711 sck pin

struct stLoadcell
{
  const int calVal_eepromAdress;
  const int zeroVal_eepromAdress; 
};

static struct stLoadcell m_astLoadcells[] =
{
  {24, 28}, // 10kg load cell
  {36, 40}, // 10kg load cell
  {48, 52}, // 5 kg load cell
  {60, 64}, // 5 kg load cell
  {72, 76}, // 3 kg load cell
  {84, 88}, // 3 kg load cell
  // {96, 100},
};

//HX711 constructor:
HX711_ADC LoadCell(HX711_dout, HX711_sck);

const int calVal_eepromAdress = m_astLoadcells[Num_LoadCell].calVal_eepromAdress;
const int zeroVal_eepromAdress = m_astLoadcells[Num_LoadCell].zeroVal_eepromAdress;

unsigned long t = 0;

void calibrate();
void changeSavedCalFactor();

void setup() {
  Serial.begin(57600); delay(10);
  Serial.println();
  Serial.println("Starting...");

  LoadCell.begin();
  //LoadCell.setReverseOutput(); //uncomment to turn a negative output value to positive
  unsigned long stabilizingtime = 2000; // preciscion right after power-up can be improved by adding a few seconds of stabilizing time
  boolean _tare = true; //set this to false if you don't want tare to be performed in the next step
  LoadCell.start(stabilizingtime, _tare);
  if (LoadCell.getTareTimeoutFlag() || LoadCell.getSignalTimeoutFlag()) {
    Serial.println("Timeout, check MCU>HX711 wiring and pin designations");
    while (1);
  }
  else {
    LoadCell.setCalFactor(1.0); // user set calibration value (float), initial value 1.0 may be used for this sketch
    Serial.println("Startup is complete");
  }
  while (!LoadCell.update());
  calibrate(); //start calibration procedure
}
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

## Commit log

2024-09-28 Test calibration Test calibration example
2024-09-28 Test with eeprom Tested readings with calibration value read from eeprom Works :)
2024-10-26 First draft of schematic MISSING: plug for connecting the button and display to the controll board
    [Windtunnel_Schematic.kicad_pcb, Windtunnel_Schematic.kicad_sch, arduino_nano.kicad_sch, disp_btn.kicad_sch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]
2024-10-29 Added sub D9 and screw terminals
    [Windtunnel_Schematic.kicad_sch, arduino_nano.kicad_sch, disp_btn.kicad_sch, hx711.kicad_sch]
2024-10-31 Add Calibration values
    [Calibration_sheet.csv, Calibration_sheet.ods, two_axis_test_sheet.ods]
2024-10-31 Schematic to 0.3.0 Nearly finished Trying to mill it tomorrow
    [Windtunnel_Schematic.kicad_pcb, Windtunnel_Schematic.kicad_sch, arduino_nano.kicad_sch, disp_btn.kicad_sch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]
2024-10-31 Code: Add new calibration tool to get also the offset value for each loadcell
2024-11-01 Schematic: First version is done and working TODO: Add labling to pcb Add comments Add changes for next version, but we will not manufacture this one
    [Windtunnel_Schematic.kicad_pcb, Windtunnel_Schematic.kicad_sch, hx711.kicad_sch]
2024-11-01 Schematic: add step file for pcb to make the housing
    [Windtunnel_Schematic.step]
2024-11-03 Add arduino step file
2024-11-03 3D model contains not the arduino
    [Windtunnel_Schematic.kicad_pcb]
2024-11-07 Add raw data
    [angle_over_rotations_full_system.ods, angle_over_rotations_full_system_conv_distance.csv, angle_over_rotations_full_system_conv_distance.ods, two_axis_test_she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]
2024-11-11 Pictures, schematic, and evaluation scripts for data - ADD: Schematic pdf and png - ADD: Pictures for presentation - CHANGE: evaluation scripts to show right data output - ADD: xlsx for angle over ro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
    [angle_over_rotations_full_system.xlsx, two_axis_test_sheet.ods, two_axis_test_sheet_full_system.ods]
2024-11-14 Add to docs, schematic and general calculation: ADD prototype data Change Schematic revision to 0.4.0 ADD requirements.txt for each general calculation virtual environment
    [Calibration_sheet.ods, Windtunnel_Schematic.kicad_pcb, Windtunnel_Schematic.kicad_sch, arduino_nano.kicad_sch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]
2024-11-14 Add Manufacturing files for pcb
    [Windtunnel_Schematic-B_Cu.gbr, Windtunnel_Schematic-Edge_Cuts.gbr, Windtunnel_Schematic-F_Cu.gbr, Windtunnel_Schematic-NPTH-drl_map.gbr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]
